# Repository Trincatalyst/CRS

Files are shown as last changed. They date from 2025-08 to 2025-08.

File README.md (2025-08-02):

# Circadian Rave System (CRS)

<p align="center">
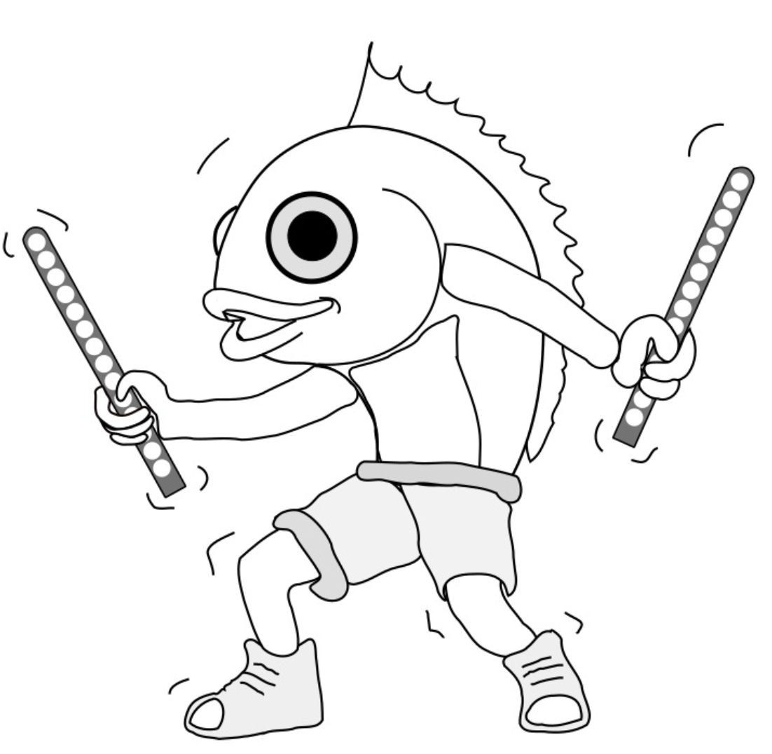
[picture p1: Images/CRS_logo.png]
CRS logo
  
</p>

__Overview of the CRS__

We have designed an affordable, high-precision, and compact system that enables users to perform light manipulation experiments on a variety of organisms. This system was designed for in laboratories specifically in incubators and has been successfully used at 15 – 30°C, and the software has been tested on both windows and mac.
Key features of the CRS include:

- Fully programmable LEDs allowing lighting paradigms that can last years
- Each unit consists of six independent lighting channels giving the user scalability of experimental arms
- The system uses an Arduino controller making the system accessible and affordable
- 
<p align="center">
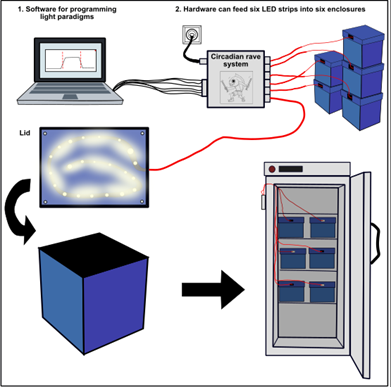
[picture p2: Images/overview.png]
System overview
  
</p>
A user via a PC app can design any conceivable light regime for each of the LED strips (currently up to 6). The PC app will then send this information to the controller which will control the brightness and timings of the LED strips for the duration of the experiments.

__Installing firmware__

The CRS firmware consists of a definition.h file and a CircadianRaveSystem.ino file, and both can be found in the GitHub repository folder titled “firmware”, or at the end of this document.

1.)	Download and install the Arduino IDE software from the [Arduino website](https://www.arduino.cc/software). 

2.)	In the Arduino IDE software select the correct Arduino COM port. Next go to file>Open… and select the folder containing the definition.h and CircadianRaveSystem.ino files.
<p align="center">
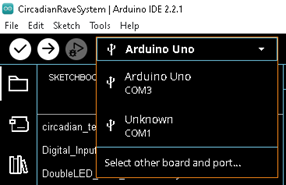
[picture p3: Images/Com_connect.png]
com port selection
  
</p>
3.)	Once a new window opens, click verify and upload to install firmware on the Arduino. The output should display this:
<p align="center">
  upload of firmware
</p>
4.)	Disconnect the now ready to use Arduino.

__Testing the CRS__

Prior to running experiments with the CRS, we suggest testing that each LED strip of the CRS works reliably for a couple of days. To do this run the CRS_test_profile.txt file found in the CRS/Software/Test. Go to Loading profiles section for instructions on how to run the CRS_test_profile file.

__Running an experiment on the CRS__

The CRS software can be directly downloaded and installed from CRS/Software/bin/. The software has been tested on both mac and Windows operating systems:
- For Windows 10 and 11 download Circadian-Rave-System-v1.2.exe file
- For macOS Ventura download Circadian-Rave-System-v1.2.dmg file
  
__Connecting to CRS hardware__

Power on the CRS and connect to the computer with the FTDI lead using the horizontal pins on the PCB. Open CRS software and in the View tab click the ‘Select Port’ dropdown menu, select the Arduino and click connect and the six LED tables should all update when connected. If experiments were running, each profile would update accordingly. Each CRS LED strip is now ready to be programmed.

<p align="center">
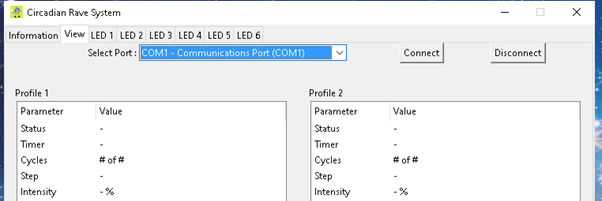
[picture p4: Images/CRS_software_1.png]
CRS software connect to device
  
</p>

__Programming the CRS__

The CRS was designed with Circadian experiments in mind and we have tried to add as much functionality as possible. Each LED can be independently programmed using the LED tabs (See top of figure below). The example profile below is a program that has a 1 second 0% light followed by 100 cycles of step 2. Step 2 is 12 hours of 100% light (T2) followed by 12 hours of 0% light (T4), mimicking  day/night cycle. T1 and T3 are the ramp up and down periods between day and night each lasting 1 second, and the ramp button is set to LINEAR, referring to the function of the light ramping.

<p align="center">
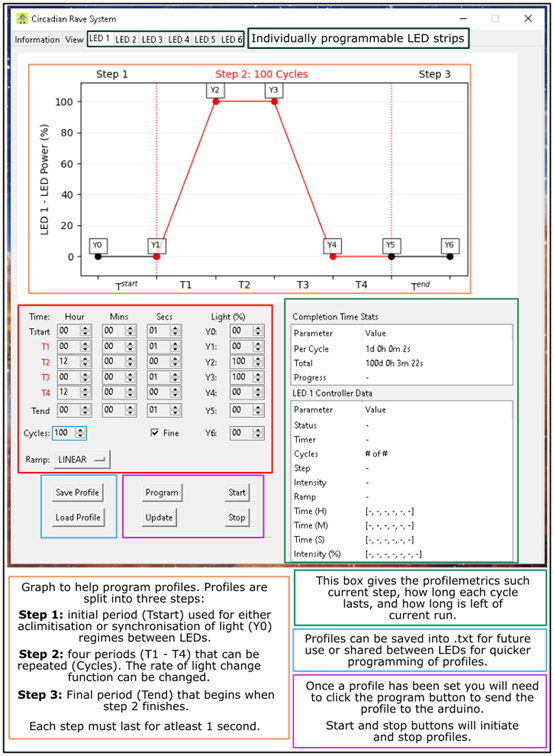
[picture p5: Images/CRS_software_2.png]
Example profile 1
  
</p>

Here is another example of a profile where the ramping function has been changed to an exponential function and that the ramping periods both last 12 hours. This is an example of a profile that might better reflect true changes in light levels through out the day.

<p align="center">
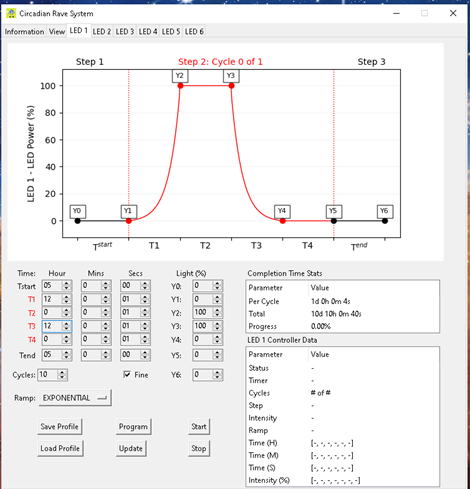
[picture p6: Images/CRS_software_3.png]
Example profile 2
  
</p>

__Saving and loading light profiles__
-	__Saving profiles__
  
Once a desired profile has been made we recommend saving it using the Save Profile button. The profile is saved to a text file that can be read by the software to program concurrently running LED profiles or future experiments.
 
-	__Loading Profiles__
  
 For testing, we recommend running the tester profile for each LED strip simultaneously. Go to the LED tabs, click on the Load profile and click on the CRS_test_profile.txt. Click Program to upload the profile into the CRS and the graph should update along with the profile statistics. Click start and the graph will live update with the progress of the run. Repeat this for all six LED profiles.

__Disconnecting from CRS hardware__

Disconnect with the Disconnect button located in the view tab, the FTRI lead can now be safely removed at this point. 

<p align="center">
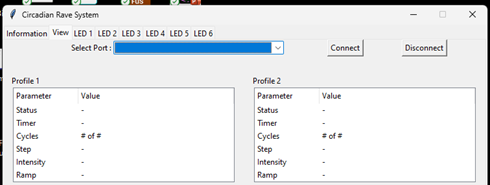
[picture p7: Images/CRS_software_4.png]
Disconnect from device
  
</p>

__Checking progress of experiments__

Whilst the CRS is running the status of profiles can be checked by simply following the connecting to hardware section. The view tab has all current information of all 6 LED tabs. Disconnect as previously described.

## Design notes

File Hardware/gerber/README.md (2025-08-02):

# gerber files

A single microcontroller_PCB file is required per device and up to six LED_PCBs can be installed and run per device.

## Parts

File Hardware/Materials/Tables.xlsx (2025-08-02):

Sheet: RAW
Reference Designator | Qty | Value | Description | Distributor Part Number | Link | Price (excl. VAT) | Total
J1 | 1 |  | Barrel Jack | Farnell 224959 | FC68148 Cliff Electronic Components, DC Power Connector, DC10A, Jack | Farnell UK (https://uk.farnell.com/cliff-electronic-components/fc68148/socket-pcb-dc-power-2-1mm-pk10/dp/224959) | £5.58 | 5.58
J4 | 6 |  | 2.54mm pitch Through Hole Header Horizontal Mount - FTDI | Farnell 3756363 | M20-9960646 Harwin, Pin Header, Board-to-Board, 2.54 mm | Farnell UK (https://uk.farnell.com/harwin/m20-9960646/conn-r-a-header-6pos-1row-2-54mm/dp/3756363) | £0.273 | 1.638
J2, J3, J5, J6, J7, J8 | 6 |  | Screw Terminals | Farnell 3767630 | 691137710002 Wurth Elektronik, Wire-To-Board Terminal Block, 5 mm, 2 Ways | Farnell UK (https://uk.farnell.com/wurth-elektronik/691137710002/tb-wire-to-brd-r-a-2way-12awg/dp/3767630) | £0.32 | 1.932
A1 - 3 way | 1 |  | Arduino Headers 3 way | Farnell 1593412 | 2211S-03G Multicomp Pro, Pin Header, Board-to-Board, 2.54 mm | Farnell UK (https://uk.farnell.com/multicomp-pro/2211s-03g/conn-hdr-3pos-1row-2-54mm/dp/1593412) | £0.03 | 0.026
A1 - 8 way | 1 |  | Arduino Headers 8 way | Farnell 1593416 | 2211S-08G Multicomp Pro, Pin Header, Board-to-Board, 2.54 mm | Farnell UK (https://uk.farnell.com/multicomp/2211s-08g/connector-header-tht-2-54mm-8way/dp/1593416) | £0.08 | 0.0828
A1 - 10 way | 1 |  | Arduino Headers 10 way | Farnell 1593417 | 2211S-10G Multicomp Pro, Pin Header, Board-to-Board, 2.54 mm | Farnell UK (https://uk.farnell.com/multicomp/2211s-10g/header-tht-vertical-2-54mm-10way/dp/1593417) | £0.09 | 0.092
Q1,Q2,Q3,Q4,Q5,Q6 | 6 | STP30NF10 | ST Microelectronics N-Channel MOSFET STP30NF10 | Farnell 9946403 | STP30NF10 Stmicroelectronics, Power MOSFET, N Channel, 100 V | Farnell UK (https://uk.farnell.com/stmicroelectronics/stp30nf10/mosfet-n-to-220/dp/9946403) | £1.53 | 9.18
R1,R3,R5,R7,R9,R11 | 6 | 100 | 100ohm axial THT resistor 250mW | Farnell 3496799 | CFR-25JT-52-100R Yageo, Through Hole Resistor, 100 ohm, CFR Series | Farnell UK (https://uk.farnell.com/yageo/cfr-25jt-52-100r/res-100r-5-0-25w-axial-carbon/dp/3496799) | £0.035 | 0.21
R2,R4,R6,R8,R10,R12 | 6 | 100k | 100kohm axial THT resistor 250mW | Farnell 3951804 | CFR-25JR-52-100K Yageo, Through Hole Resistor, 100 kohm, CFR Series | Farnell UK (https://uk.farnell.com/yageo/cfr-25jr-52-100k/res-100k-0-25w-axial-carbon/dp/3951804) | £0.036 | 0.2154
D1 | 1 |  | Diode | Farnell 4245041 | 1N4001 Multicomp Pro, Standard Recovery Diode, 50 V, 1 A | Farnell UK (https://uk.farnell.com/multicomp-pro/1n4001/rectifier-single-50v-1a-do-204al/dp/4245041) | £0.08 | 0.0787
U1 | 1 |  | eFuse Circuit Protection | Farnell 4178928 | LS0504EVT233 Littelfuse, Hot-Swap Controller, Electronic Fuse, 2.7 V to 6 V | Farnell UK (https://uk.farnell.com/littelfuse/ls0504evt233/electronic-fuse-40-to-150deg-c/dp/4178928) | £0.57 | 0.575
C3, C4 | 2 | 0.1uF | 0.1uF Ceramic Capacitor | Farnell 2507749 | K104K10X7RF5UH5 Vishay, Multilayer Ceramic Capacitor, 0.1 µF, 50 V | Farnell UK (https://uk.farnell.com/vishay/k104k10x7rf5uh5/cap-0-1-f-50v-10-x7r/dp/2507749) | £0.09 | 0.1758
C1, C2 | 2 | 1uF | 1uF Ceramic Capacitor | Farnell 2819603 | C410C105K3R5TA Kemet, Multilayer Ceramic Capacitor, 1 µF, 25 V | Farnell UK (https://uk.farnell.com/kemet/c410c105k3r5ta/cap-1-f-25v-10-x7r/dp/2819603) | £0.08 | 0.154
 | 1 |  | POWER SUPPLY 15W | Farnell 2815857 | GST18A05-P1J Mean Well, AC/DC Power Supply, ITE, 1 Output | Farnell UK (https://uk.farnell.com/mean-well/gst18a05-p1j/adaptor-ac-dc-5v-3a/dp/2815857) | £19.89
 | 1 |  | FTDI Cable | Farnell 2419945 | TTL-232R-5V Ftdi, USB to Serial Converter Cable, 5V, 6Way | Farnell UK (https://uk.farnell.com/ftdi/ttl-232r-5v/usb-to-serial-converter-cable/dp/2419945) | £19.41 | 19.0349
 |  |  |  |  | Arduino

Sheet: table_1
Table 1: List of all parts required to build Circadian Rave System
Component | Source (Part Number) | Quantity
Barrel Jack | Farnell (224959) | 1
2.54mm pitch Through Hole Header Horizontal Mount - FTDI | Farnell (3756363) | 6
Screw Terminals | Farnell (3767630) | 6
Arduino Headers 3 way | Farnell (1593412) | 1
Arduino Headers 8 way | Farnell (1593416) | 1
Arduino Headers 10 way | Farnell (1593417) | 1
ST Microelectronics N-Channel MOSFET STP30NF10 | Farnell (9946403) | 6
100ohm axial THT resistor 250mW | Farnell (3496799) | 6
100kohm axial THT resistor 250mW | Farnell (3951804) | 6
Diode | Farnell (4245041) | 1
eFuse Circuit Protection | Farnell (4178928) | 1
0.1uF Ceramic Capacitor | Farnell (2507749) | 2
1uF Ceramic Capacitor | Farnell (2819603) | 2
POWER SUPPLY 15W | Farnell (2815857) | 1
FTDI Cable | Farnell (2419945) | 1
Arduino Uno R3 | Arduino (A000066) | 1
LEDs | RS (855-5933) | 120*
Circadian Rave System PCB | Martin Lab* | 1
*120 strips or 1 LED component with a LED PCB

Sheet: table_2
Table 2: Component references for circuit constructions
Component | Circuit Reference
Barrel Jack | J1
2.54mm pitch Through Hole Header Horizontal Mount - FTDI | J4
Screw Terminals | J2, J3, J5, J6, J7, J8
Arduino Headers 3 way | A1 - 3 way
Arduino Headers 8 way | A1 - 8 way
Arduino Headers 10 way | A1 - 10 way
ST Microelectronics N-Channel MOSFET STP30NF10 | Q1,Q2,Q3,Q4,Q5,Q6
100ohm axial THT resistor 250mW | R1,R3,R5,R7,R9,R11
100kohm axial THT resistor 250mW | R2,R4,R6,R8,R10,R12
Diode | D1
eFuse Circuit Protection | U1
0.1uF Ceramic Capacitor | C3, C4
1uF Ceramic Capacitor | C1, C2

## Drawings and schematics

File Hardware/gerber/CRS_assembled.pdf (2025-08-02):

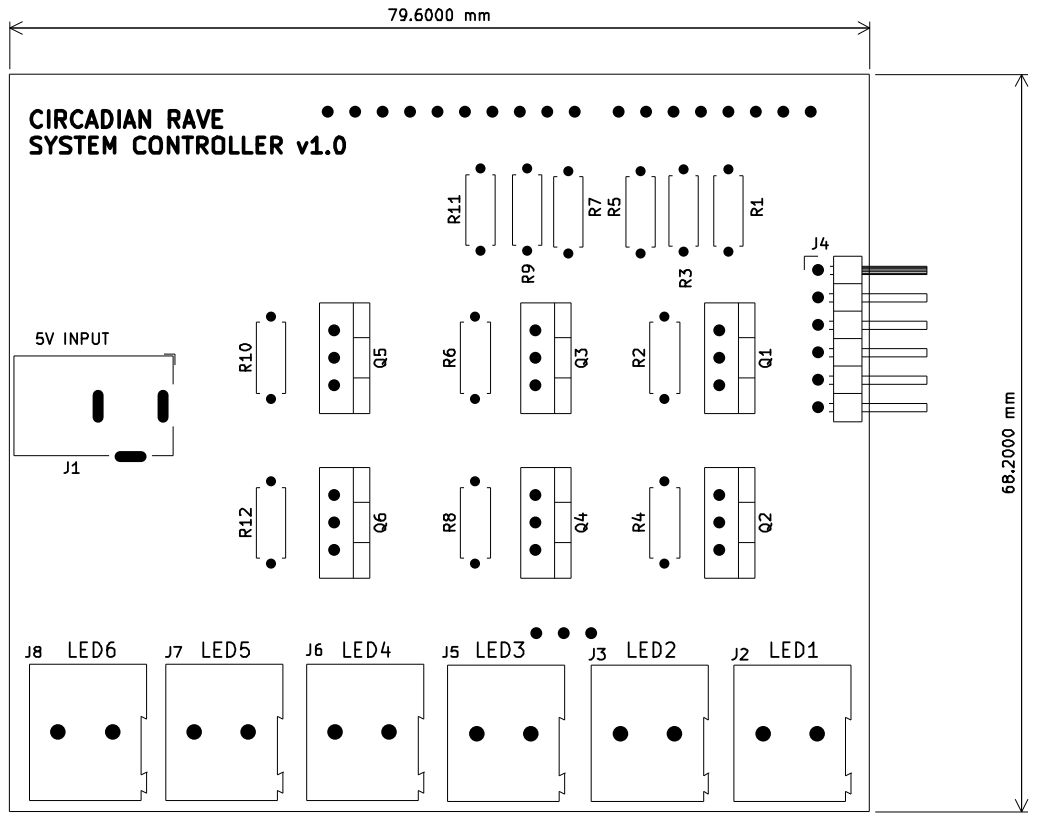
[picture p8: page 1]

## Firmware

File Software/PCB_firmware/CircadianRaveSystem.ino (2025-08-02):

#include "definitions.h"

// Global Variables
ProfileStruct_TypeDef profiles_arr[NUM_LED_STRIPS];
CommandStruct_TypeDef cmd_struct;
ValidCommandStruct_TypeDef commands[NUM_COMMANDS];
uint32_t time_last = 0;
uint8_t buffer_index = 0; // Index to keep track of the current position in the buffer
uint8_t led_status = 0;
uint8_t led_pins[6] = {LED1_PIN, LED2_PIN, LED3_PIN, LED4_PIN, LED5_PIN, LED6_PIN};
char input_buffer[RX_BUFFER_SIZE]; // Buffer to store the incoming string
float exp_lut[NUM_POINTS] = {0.00, 0.05, 0.10, 0.15, 0.20, 0.26, 0.32, 0.38, 0.45, 0.51, 0.59, 0.66, 0.74, 0.82, 0.91, 1.00, 1.09, 1.19, 1.29, 1.40, 1.52, 1.64, 1.76, 1.89, 2.03, 2.17, 2.32, 2.48, 2.64, 2.81, 2.99, 3.18, 3.38, 3.59, 3.80, 4.03, 4.27, 4.52, 4.78, 5.05, 5.33, 5.63, 5.95, 6.28, 6.62, 6.98, 7.36, 7.75, 8.16, 8.60, 9.05, 9.52, 10.02, 10.54, 11.09, 11.66, 12.26, 12.88, 13.54, 14.22, 14.94, 15.70, 16.49, 17.31, 18.18, 19.08, 20.03, 21.02, 22.06, 23.15, 24.29, 25.49, 26.74, 28.05, 29.42, 30.86, 32.36, 33.94, 35.59, 37.32, 39.13, 41.02, 43.01, 45.09, 47.26, 49.54, 51.93, 54.43, 57.05, 59.79, 62.66, 65.67, 68.82, 72.12, 75.57, 79.19, 82.97, 86.94, 91.09, 95.44, 100.00};


void setup() 
{
  Serial.begin(BAUDRATE);
  pwm_init();
  setup_valid_commands();
  
  #ifdef TEST
  Serial.print("TEST BUILD: DEBUGGING ON\n");
  Serial.print("---- Circadian Rave System ----\n");
  #endif

  // Create and initialize the profile structures
  for(int i=0; i<NUM_LED_STRIPS; i++)
  {
    profiles_arr[i] = init_profile_struct();
    profiles_arr[i].index = i + PROFILE_INDEX_START;
    profiles_arr[i].led_pin = led_pins[i];
  }

  // Setup Arduino LED Pins
  pinMode(13, OUTPUT);
  
}

void loop() 
{
  serial_read();

  // update the profiles that are running every one second.
  if (millis() - time_last > ONE_SECOND)
  {
    time_last = millis();
    //Serial.println(millis());

    // LED Flash every 1 second
    led_status = !led_status; // toggle status
    digitalWrite(13, led_status);
  
    // Go through each profile to update the data
    for(int i=0; i<NUM_LED_STRIPS; i++)
    {
      //only update the profiles that are running
      if (profiles_arr[i].profile_status == RUNNING)
      {
        update_profile(&profiles_arr[i]);
      }
    }
  }
}

// FUNCTIONS START HERE

void pwm_init(void)
{
  for(int i=0; i<NUM_LED_STRIPS; i++)
  {
    pinMode(led_pins[i], OUTPUT);
    analogWrite(led_pins[i], 0);
  }

  // Set Timer 0 (controls pins 5 and 6)
  TCCR0B =  (1 << CS01)|(1 << CS00); // Prescalar = 64. 16M/64/255 so PWM frequency is 980 Hz

  // Set Timer 1 (controls pins 9 and 10)
  // Timer 1 is a 16-bit timer so I am assuming it is setup as an 8 bit resolution
  TCCR1B = (1 << CS11)|(1 << CS10); // // Prescalar = 64 so PWM frequency is around 980 Hz
  
  // Set Timer 2 (controls pins 3 and 11)
  TCCR2B =  (1 << CS22); // Prescalar = 64 so PWM frequency is around 980 Hz
}

void update_profile(ProfileStruct_TypeDef* profile)
{
  uint32_t T1 = profile->time_vals[1];
  uint32_t T5 = profile->time_vals[5];
  uint32_t TEND = profile->time_vals[6];
  uint32_t T5_actual = T1 + (profile->num_cycles*(T5-T1));
  uint32_t time;

  // update the timer
  profile->timer_seconds += 1; 
  time = profile->timer_seconds;

  // update which step the profile is on
  if(time < T1)
  { // STEP 1
      profile->current_step = STEP1;
  }
  
  if(time >= T1 && time < T5_actual)
  { // STEP 2
      profile->current_step = STEP2;
      // update the current cycle variable as well.
      profile->current_cycle = 1 + ((time - T1)/(T5-T1));
  }

  if(time >= T5_actual)
  { // STEP 3
    profile->current_step = STEP3;
  }

  if(time >= TEND)
  {
    profile->current_step = COMPLETE;
  }

  // update the led intensity.
  update_led_intensity(profile);    
}

void update_led_intensity(ProfileStruct_TypeDef* profile)
{
  // function looks at the profile and calculates the LED intensity by linear interpolation
  uint32_t T1 = profile->time_vals[1];
  uint32_t T5 = profile->time_vals[5];
  uint32_t time = profile->timer_seconds;
  uint16_t pwm_duty = 0;
  uint32_t x = 0;  // time point based on where in the cycle we are

  if(profile->current_step == STEP1)
  {
    x = time;
    profile->current_intensity = map(x, profile->time_vals[0], profile->time_vals[1], profile->intensity_vals[0], profile->intensity_vals[1]);
    if (profile->curve == CURVE_LINEAR)
    {
      pwm_duty = map(profile->current_intensity, 0, 100, 0, PWM_TOP); 
    }
    if (profile->curve == CURVE_EXPONENTIAL)
    {
      profile->current_intensity  = exp_lut[profile->current_intensity];
      pwm_duty = map(profile->current_intensity, 0, 100, 0, PWM_TOP);
    }
    analogWrite(profile->led_pin, pwm_duty);
  }

  if(profile->current_step == STEP3)
  {
    x = time - T5;
    profile->current_intensity = map(x, profile->time_vals[5], profile->time_vals[6], profile->intensity_vals[5], profile->intensity_vals[6]);
    if (profile->curve == CURVE_LINEAR)
    {
      pwm_duty = map(profile->current_intensity, 0, 100, 0, PWM_TOP); 
    }
    if (profile->curve == CURVE_EXPONENTIAL)
    {
      profile->current_intensity  = exp_lut[profile->current_intensity];
      pwm_duty = map(profile->current_intensity, 0, 100, 0, PWM_TOP);
    }
    analogWrite(profile->led_pin, pwm_duty);
  }

  // If the profile is complete, then turn LED off.
  if(profile->current_step == COMPLETE)
  {
    profile->current_intensity = 0;
    analogWrite(profile->led_pin, 0);
  }

  if(profile->current_step == STEP2)
  {
    x = ((time - T1) % (T5-T1)) + T1;
    
    // using the timepoint x, find the index where it falls
    uint8_t i = 0;
    for (i = 0; i < NUM_TIME_VAL_PAIRS; i++) {
        if (x <= profile->time_vals[i+1]) {
            break;
        }
    }
    
    profile->current_intensity = map(x, profile->time_vals[i], profile->time_vals[i+1], profile->intensity_vals[i], profile->intensity_vals[i+1]);
    if (profile->curve == CURVE_LINEAR)
    {
      pwm_duty = map(profile->current_intensity, 0, 100, 0, PWM_TOP);
    } 
    if (profile->curve == CURVE_EXPONENTIAL)
    {
      profile->current_intensity  = exp_lut[profile->current_intensity];
      pwm_duty = map(profile->current_intensity, 0, 100, 0, PWM_TOP);
    }
    analogWrite(profile->led_pin, pwm_duty);
  }  

}

// Function to check if an array is monotonically increasing
bool is_increasing(uint32_t* array, int size)
{
  bool increasing = true;
  if (size <= 1) 
  {
    return true; // An array with 0 or 1 elements is monotonic by definition
  }
  for (int i = 1; i < size; ++i) 
  {
    if (array[i] <= array[i - 1]) 
    {
      increasing = false;
    }
  }
  return increasing;
}

void send_packet(ProfileStruct_TypeDef* profiles)
{
  //"status, time, num_cycles, current_step, current_cycle, current_intensity, curve
  for(int i=0; i<NUM_LED_STRIPS; i++)
  { 
    Serial.print("{P");
    Serial.print(profiles[i].index);
    Serial.print(",");
    Serial.print(profiles[i].profile_status);
    Serial.print(",");
    Serial.print(profiles[i].timer_seconds);
    Serial.print(",");
    Serial.print(profiles[i].num_cycles);
    Serial.print(",");
    Serial.print(profiles[i].current_step);
    Serial.print(",");
    Serial.print(profiles[i].current_cycle);
    Serial.print(",");
    Serial.print(profiles[i].current_intensity);
    Serial.print(",");
    Serial.print(profiles[i].curve);
    Serial.print(",[");

    for(int j=0; j<NUM_TIME_VAL_PAIRS; j++)
    {
        Serial.print(profiles[i].time_vals[j]);
        if(j<NUM_TIME_VAL_PAIRS-1){
          Serial.print(",");
        }
    }
    Serial.print("],[");

    for(int j=0; j<NUM_TIME_VAL_PAIRS; j++)
    {
        Serial.print(profiles[i].intensity_vals[j]);
        if(j<NUM_TIME_VAL_PAIRS-1){
          Serial.print(",");
        }
    }
    Serial.print("]},");
    #ifdef TEST
      Serial.print("]}\n");
    #else
      Serial.print("]},");
    #endif
  }
  Serial.println("PEACE-OUT!");

}

void valid_command_response(CommandStruct_TypeDef* cmd_struct)
{
  #ifdef TEST
  Serial.print(float(millis()/1000.0), 2);
  Serial.print("s -> COMMAND OK: ");
  Serial.print(cmd_struct->cmd);
  Serial.print(" ");
  Serial.print(cmd_struct->profile_index); 
  Serial.print(" ");
  Serial.print(cmd_struct->val1);
  Serial.print(" ");
  Serial.print(cmd_struct->val2);
  Serial.print("\n");
  send_packet(profiles_arr);  // THIS IS TEMPORARY
  #endif
}


uint8_t get_profile_index(CommandStruct_TypeDef* cmd_struct)
{
  // Returns the profile index based on the c indexing scheme. 
  // Profile 1 might be index 0, so it returns 0
  return (cmd_struct->profile_index) - PROFILE_INDEX_START;
}

uint8_t get_time_index(CommandStruct_TypeDef* cmd_struct)
{
  // returns the time index. So T1 is index 0
  uint8_t time_index;
  sscanf(cmd_struct->cmd, "set_T%d", &time_index);
  //time_index = time_index - 1;
  return time_index;
}

void invalid_command_response(char* response)
{
  #ifdef TEST
  Serial.print((float)(millis()/1000.0), 2);
  Serial.print("s -> BAD COMMAND: ");
	Serial.println(response);
  #endif
}
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

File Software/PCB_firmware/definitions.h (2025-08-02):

#define BAUDRATE 115200

//#define TEST // comment out if in production

#define ONE_SECOND 999

// Pins
#define LED1_PIN  3
#define LED2_PIN  5
#define LED3_PIN  6
#define LED4_PIN  9
#define LED5_PIN  10
#define LED6_PIN  11


#define STEP1   1
#define STEP2   2
#define STEP3   3
#define COMPLETE 4


#define PWM_TOP 255

// Profile Status definitions
#define NOT_STARTED 0
#define RUNNING 1

#define RX_BUFFER_SIZE 70

#define CURVE_LINEAR 0
#define CURVE_EXPONENTIAL 1
#define NUM_POINTS 101

// Command Status definitions
#define CMD_OK 1        // command received ok
#define CMD_ERROR 100   // command error

#define NUM_TIME_VAL_PAIRS 7
#define NUM_LED_STRIPS 6

#define PROFILE_INDEX_START 1 // Either 0 or 1

#define NUM_COMMANDS 13

#define CMD_GET_STATUS  "get_status"
#define CMD_START       "start"
#define CMD_STOP        "stop"
#define SET_CYCLES      "set_cycles"
#define SET_CURVE       "set_curve"
#define SET_T0          "set_T0"
#define SET_T1          "set_T1"
#define SET_T2          "set_T2"
#define SET_T3          "set_T3"
#define SET_T4          "set_T4"
#define SET_T5          "set_T5"
#define SET_T6          "set_T6"
#define RESET_PROFILES  "reset_profiles"

#define DEFAULT_TSRART_DURATION 10
#define DEFAULT_T1_DURATION 10
#define DEFAULT_T2_DURATION 10
#define DEFAULT_T3_DURATION 10
#define DEFAULT_T4_DURATION 10
#define DEFAULT_TEND_DURATION 10

typedef struct Profile{
  uint8_t index;
  uint32_t timer_seconds;
  uint8_t led_pin;
  uint8_t profile_status;
  uint16_t num_cycles;
  uint16_t current_cycle;
  uint8_t current_step;
  uint8_t curve;
  uint8_t current_intensity;
  uint32_t time_vals[NUM_TIME_VAL_PAIRS];
  uint8_t intensity_vals[NUM_TIME_VAL_PAIRS];
} ProfileStruct_TypeDef;

typedef struct Command{
  char cmd[15];
  uint8_t profile_index;
  uint32_t val1;
  uint32_t val2;
} CommandStruct_TypeDef;

typedef struct ValidCommands{
  char cmd[15];
} ValidCommandStruct_TypeDef;


// Function declerations
void pwm_init(void);
ProfileStruct_TypeDef init_profile_struct();
void command_reset(CommandStruct_TypeDef* cmd_struct);
void process_command(CommandStruct_TypeDef* cmd_struct, ProfileStruct_TypeDef* profiles, char* buffer);
void send_packet(ProfileStruct_TypeDef* profiles);
void serial_read(void);
uint8_t command_digest(CommandStruct_TypeDef* cmd_struct);
void setup_valid_commands();
void valid_command_response(CommandStruct_TypeDef* cmd_struct);
uint8_t get_profile_index(CommandStruct_TypeDef* cmd_struct);
uint8_t get_time_index(CommandStruct_TypeDef* cmd_struct);
bool is_increasing(uint32_t* array, int size);
void update_led_intensity(ProfileStruct_TypeDef* profile);
void update_profile(ProfileStruct_TypeDef* profile);
void reset_profiles(void);
